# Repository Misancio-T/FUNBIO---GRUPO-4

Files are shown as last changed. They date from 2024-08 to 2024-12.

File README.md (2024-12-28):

<p align="center">
  <img src="[https://fundbio.github.io/images/pucp_upch.png]>
</p>

(https://postimg.cc/rDdD7Vwj)
---

<h1><p align="center"> Proyecto de FUNBIO - Equipo 4 ☕️ </p></h1>

¡Bienvenidos! Somos el Grupo 4 del Curso de Fundamentos de Biodiseño, Código: 1CAY41, dictado
en el semestre 2024-2 por la carrera de Ingeniería Biomédica PUCP - UPCH

## Temática de nuestro horario 📜

Lesiones Medulares

## Link de nuestro repositorio 🔗

 : github.com/Misancio-T/FUNBIO---GRUPO-4.git

## Link de nuestra página web 🌎

 : https://uyariy.tech

## Nos presentamos... 

<h3>ANGIE HUÁNUCO VÁSQUEZ (Coordinadora General)</h3>

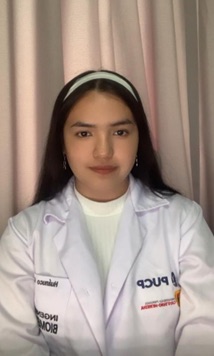
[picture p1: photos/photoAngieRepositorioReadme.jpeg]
fotoAngie
> 
> <h4> Me presento</h4>
>
> <p align="justify"> Soy estudiante de Ingeniería Biomédica con interés en el desarrollo y mejora de dispositivos médicos que permitan mejorar las condiciones de vida de las personas.  </p>
> <h4> Rol en el equipo</h4>
> <p align="justify"> Mi rol durante el curso es de Coordinadora General. Soy responsable de supervisar el avance del proyecto en su totalidad, asegurando que cada fase se ejecute según el plan establecido. Coordino las tareas entre los diferentes miembros del equipo, facilitando la comunicación y resolviendo cualquier problema que pueda surgir. Además, me encargo de la planificación de reuniones y la elaboración de los 'entregables' respecto al progreso del proyecto. </p>
> <h4> Rama de interés</h4>
> <p align="justify"> Procesamiento de señales e imágenes biomédicas. </p>

<h3>Misael Torres Bautista (Diseñador 3D)</h3>

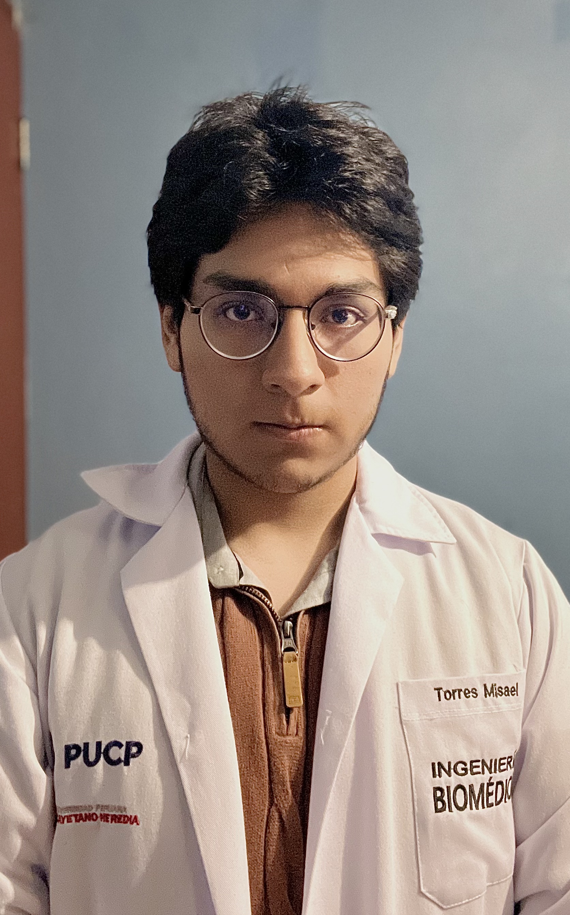
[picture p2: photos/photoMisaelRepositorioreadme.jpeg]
fotoMisael
> 
> <h4> Me presento</h4>
>
> <p align="justify"> Soy estudiante de Ingeniería Biomédica en la Pontificia Universidad Católica del Perú y la Universidad Peruana Cayetano Heredia. Busco desarrollar dispositivos médicos para mejorar la salud en el Perú. Mi objetivo es usar los conocimientos adquiridos a lo largo del curso para aplicar estas herramientas en un futuro.  </p>
> <h4> Rol en el equipo</h4>
> <p align="justify"> Mi rol en este proyecto es el de Diseñador 3D. Soy responsable de crear los modelos 3D basados en los bocetos y propuestas de solución desarrolladas por el equipo. Utilizo herramientas como INVENTOR, BLENDER, CINEMA 4D Y ULTIMAKER CURA para diseñar y preparar los modelos para su impresión. También me encargo de gestionar y actualizar el repositorio de GitHub del equipo.  </p>
> <h4> Rama de interés</h4>
> <p align="justify"> Ingeniería de tejidos y la biomecánica. </p>

<h3>Silvana Villegas Berrocal (Manufactura Digital)</h3>

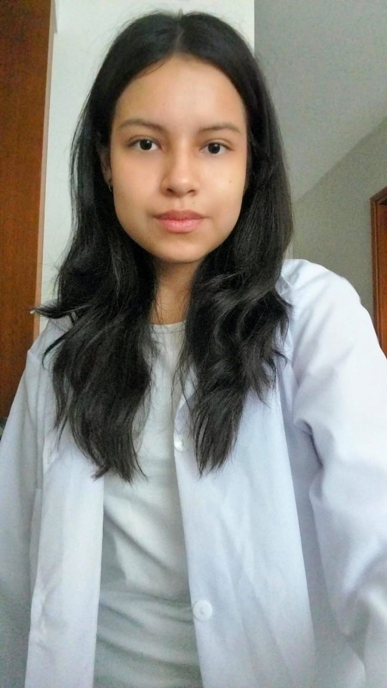
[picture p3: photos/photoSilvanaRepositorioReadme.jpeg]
fotoSilvana
> 
> <h4> Me presento</h4>
>
> <p align="justify"> Soy estudiante de Ingeniería Biomédica. Mi objetivo es la investigación de los cambios del cuerpo humano en diferentes ambientes para maximizar las capacidades físicas. </p>
><h4> Rol en el equipo</h4>
> <p align="justify"> Mi rol es diseñar y gestionar los procesos de manufactura digital, asegurando la calidad y precisión en la creación de prototipos. </p>
> <h4> Rama de interés</h4>
> <p align="justify"> Ingeniería molecular y celular así como sistemas biológicos. </p>

<h3>Sydnee Yampara Mamani (Prototipo Electrónico)</h3>

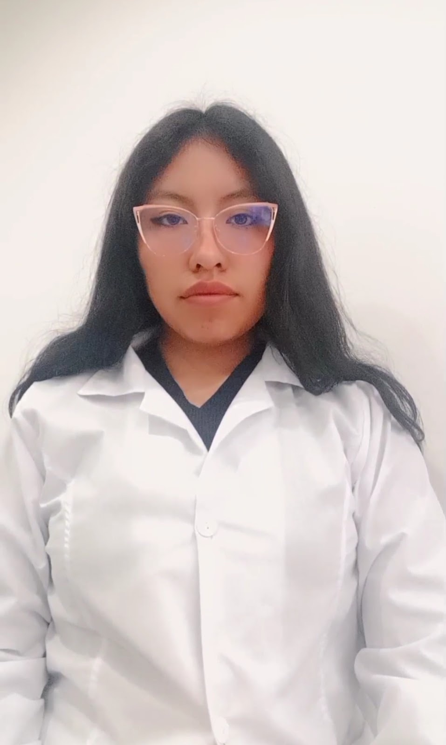
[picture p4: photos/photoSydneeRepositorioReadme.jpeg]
fotoSydnee
> 
> <h4> Me presento</h4>
> <p align="justify"> Soy estudiante de ing biomédica con objetivo de innovación e ideas de tecnología relacionada a la salud para la implementación descentralizada de equipos médicos y detección no invasiva de las distintas enfermedades. </p>
> <h4> Rol en el equipo</h4>
> <p align="justify"> Mi rol es diseñar y desarrollar prototipos electrónicos, incluyendo la selección de componentes y la integración de circuitos, para asegurar su funcionalidad y rendimiento. </p>
> <h4> Rama de interés</h4>
> <p align="justify"> Ingeniería clínica e ingeniería de tejidos. </p>

<h3>William Zamalloa Quispe (Diseño electrónico)</h3>

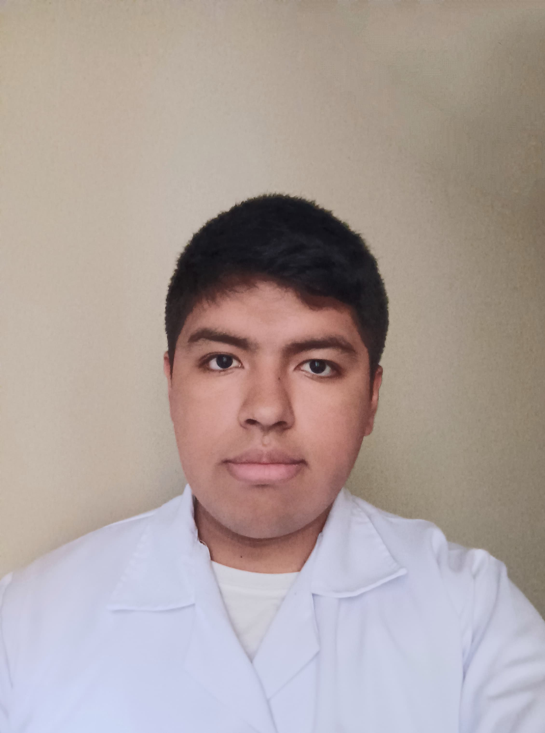
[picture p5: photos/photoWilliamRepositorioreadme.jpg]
fotoWilliam
> 
> <h4> Me presento</h4>
> <p align="justify"> Soy estudiante de ingeniería biomédica, poseo interés en la mejora y desarrollo de prótesis para el cuerpo humano, espero trabajar con prótesis sencillas y funcionales y con algunas más complejas y especializadas. </p>
> <h4> Rol en el equipo</h4>
> <p align="justify"> Mi rol es diseñar circuitos electrónicos utilizando software especializado, creando esquemas detallados y simulaciones para asegurar la eficiencia y funcionalidad de los prototipos. También administro y actualizo el repositorio de GitHub del equipo remotamente. </p>
> <h4> Rama de interés</h4>
> <p align="justify"> Biomecánica y desarrollo de prótesis avanzadas. </p>

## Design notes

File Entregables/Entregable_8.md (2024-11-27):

# Integración Hardware - Software - Manufactura Digital

## Introducción y Contextualización del Prototipo

### Descripción breve del Proyecto
El objetivo principal de este prototipo es desarrollar un sistema de retroalimentación sensorial artificial que mejore la propiocepción en personas con disminución de la percepción corporal,  se centra en proporcionar a estos pacientes un sistema que pueda suplir la retroalimentación sensorial pérdida y ayudarles a recuperar, en la medida de lo posible, la capacidad de moverse de forma segura y confiada.

Este sistema utiliza un dispositivo que mide la posición y el movimiento durante las fases de la marcha, ya sea al caminar o al estar de pie, y envía señales a unas bandas vibratorias que el usuario lleva puestas. Estas bandas vibran en tiempo real para proporcionar una retroalimentación táctil inmediata, alertando al usuario sobre su posición y movimiento.

### Problemática abordada

Este prototipo se centra en proporcionar a estos pacientes un sistema que pueda suplir la retroalimentación sensorial pérdida y ayudarles a recuperar, en la medida de lo posible, la capacidad de moverse de forma segura y confiada, todo esto a través de un sistema de feedback sensorial artificial que restaure la percepción corporal mediante retroalimentación táctil, promoviendo una rehabilitación más rápida y efectiva y aumentando la seguridad y el bienestar del paciente en su día a día.

La necesidad que motiva este proyecto es mejorar la calidad de vida de personas con lesiones medulares completas de tipo A que han perdido la capacidad de recibir retroalimentación sensorial y de controlar su motricidad mediante un dispositivo en forma de una cajita pequeña que va ajustada a una parte estratégica del pie. Esto nos ayudará a poder restaurar la pérdida de sensibilidad de nuestro paciente al momento de realizar bipedestación o marcha.  Esta pérdida de sensibilidad y control afecta significativamente su capacidad de moverse, caminar y mantenerse de pie de manera autónoma, lo que los hace depender de dispositivos de asistencia.

### Objetivos de la fase de integración

Lo que se espera al lograr integrar los componentes que forman parte de nuestra propuesta es asegurarnos de que los componentes del dispositivo (sensores, procesadores, baterías, etc) trabajen juntos de manera sincronizada para medir y registrar la proximidad del pie con el piso con precisión. A la vez, esperamos lograr que se logre comprobar los datos que los sensores envían para medir hacer las mediciones respecto a las pisadas del paciente para poder corregir errores de lectura. Finalmente, deseamos evaluar que el dispositivo sea compatible con las condiciones reales de uso, comprobando que la integración de sus componentes le permita operar correctamente en entornos de prueba similares a su aplicación final.

## Componentes del Prototipo

### Lista de componentes principales

**Componentes en la parte del pie**

- **Batería 3.7V, 720 mAh Li-Po:** Actúa como la fuente de energía para esta sección del prototipo, suministrando alimentación al Atom Matrix.
- **LiPo Rider Plus:** Este módulo sirve como intermediario entre la batería y el Atom Matrix, facilitando la carga de la batería a través de un puerto USB tipo C.
- **Atom Matrix:** Es el "cerebro" del prototipo. Integra un acelerómetro MPU-6886 que captura datos en los ejes X, Y y Z en tiempo real, así como un ESP32 PICO, un microcontrolador compacto utilizado para enviar los datos por medio de Bluetooth. Además, cuenta con una pantalla de luces LED que puede utilizarse de distintas maneras, como un indicador visual adicional, proporcionando así feedback tanto para el paciente como para el terapeuta.

**Componentes en la parte del brazo**

- **Motores Vibradores Tipo Moneda:** Similar a los que se usan en teléfonos móviles, estos motores se emplea para proporcionar retroalimentación sensorial en el brazo del usuario.
- **Batería 3.7V, 720 mAh Li-Po:** Actúa como la fuente de energía en esta sección del prototipo, suministrando alimentación al ESP32 Super Mini.
- **Módulo TP4056:** Es una versión más sencilla que el LiPo Rider Plus y permite cargar la batería Li-Po y alimentar el ESP32 Super Mini.

### Interacción entre componentes

Los componentes principales que interactúan en este prototipo son el Atom Matrix, que incluye un ESP32 PICO, y el ESP32 Super Mini ubicado en el brazo. La comunicación entre ambos se realiza mediante programación Bluetooth, estableciendo un sistema maestro-esclavo para la transmisión y recepción de datos entre los dispositivos.

### Diagrama de integración

<p align="center">
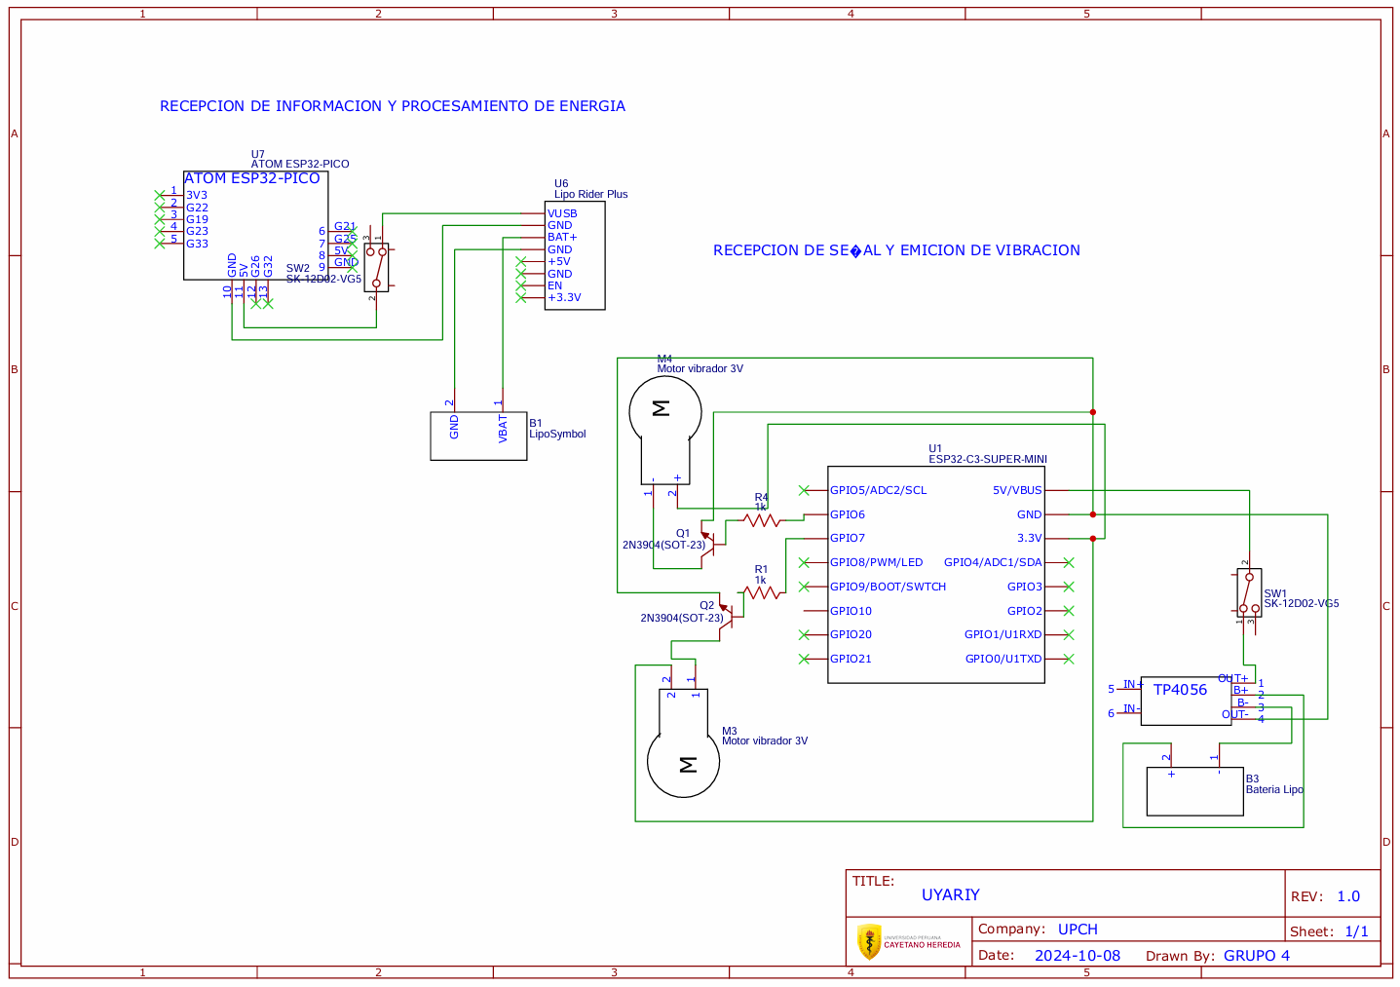
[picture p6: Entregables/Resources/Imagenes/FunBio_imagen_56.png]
Esquema Electrónico

</p>

## Proceso de Integración

### Plan Inicial de Integración

**- Paso 1:** Desarrollo del Sistema en el Pie

Configuración del ATOM PICO ESP32 para medir ángulos y convertirlos en grados de inclinación que al tener incluído el microcontrolador podemos visualizar los datos en tiempo real mediante un monitor serie con el objetivo de tener mediciones precisas y consistentes.

Para la programación del microcontrolador (pie) creamos un programa para leer datos del sensor y transmitirlos por Bluetooth al dispositivo esclavo.

Se prueban datos simulados desde el sensor a una laptop.

**- Paso 2: Desarrollo del Sistema en el Brazo (dispositivo esclavo)**

Programar el receptor Bluetooth para recibir datos enviados por el módulo del pie.  Posteriormente integrar y probar el motor de vibración para generar pulsos en función de los datos.  

Se probó simulando la recepción de ángulos y activar las luces led, momentáneas, correctamente.

**- Paso 3: Comunicación Bluetooth**

Configurar el emparejamiento del módulo transmisor del pie con el receptor del brazo para verificar la estabilidad y velocidad de la conexión Bluetooth

### Pruebas Intermedias

**1. Prueba unitaria del sensor:**

   Confirmar que el sensor mide correctamente los ángulos de inclinación.  

**2. Prueba de transmisión Bluetooth:**  
   
   Evaluar la precisión y latencia de los datos enviados desde el pie al brazo.  

**3. Prueba del motor de vibración:**  
   
   Ajustar la intensidad y duración de las vibraciones para que sean perceptibles sin ser incómodas.  

### Objetivos

1. Obtener mediciones angulares precisas del pie durante diferentes pisadas.

2. Lograr una transmisión de datos Bluetooth con baja latencia y sin interrupciones.

3. Generar una retroalimentación háptica en el brazo que sea intuitiva y fácil de interpretar.

4. Implementar un diseño ergonómico y funcional para ambos módulos.

### Desafíos y ajustes realizados

**1. Calibración del Sensor de Ángulo**

- Desafio

La lectura del sensor era inconsistente debido a interferencias de movimiento no deseado y ruido en los datos, también el cuestionamiento de medida entre el ángulo o la altura.

- Ajuste Realizado

Ajuste de los valores iniciales mediante un proceso de calibración manual para establecer un punto de referencia (offset) y decisión de medida a angulo de giro..

### Revisión de compatibilidad y sincronización

<p align="center">
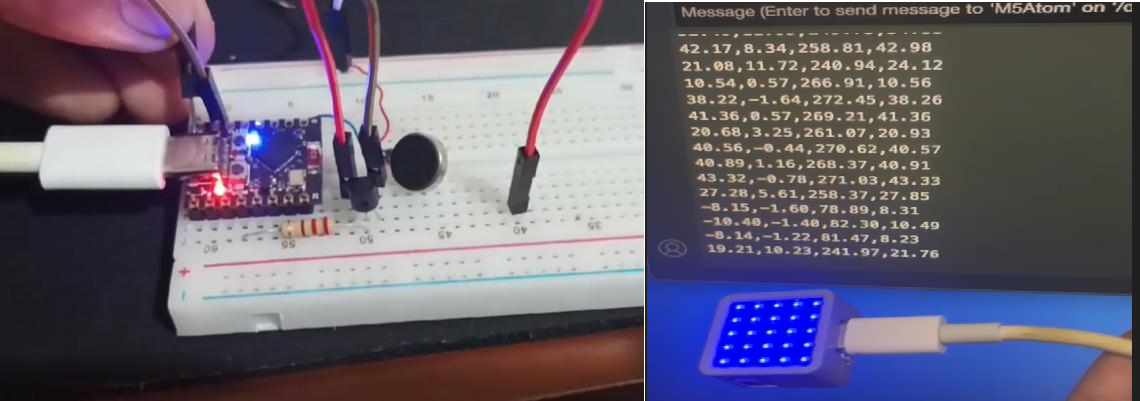
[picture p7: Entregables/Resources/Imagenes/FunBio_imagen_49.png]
Revision de componentes

</p>

## Pruebas y Verificación

### Descripción de pruebas funcionales

Los microcontroladores usados requieren más programación, para ello se usaron ejemplos presentes en Arduino y luego de comprobar su funcionamiento se procedió a probar el de componentes, en el caso de los motores vibradores para comprobar su funcionamiento se conecto el cable positivo al terminal de 3.3v de uno de los microcontroladores y el cable negativo a GND, con ello probamos que todos los componentes son funcionales y están listos para el ensamblaje en conjunto.

### Resultados de pruebas

Las primeras pruebas se esperaba lograr la activación del motor con un pin del microcontrolador pero estas pruebas resultaron fallidas debido a que se intentó usar un protoboard para realizar las conexiones del esp32 C3 con el motor vibrador y no se podía porque el esp32 no se podía conectar bien al protoboard, para ello fue necesario soldar los componentes al esp32 para comprobar su funcionamiento, otro contratiempo fue que los motores vibradores tienen un cable muy delgado que complica las conexiones además de el soldar el motor al resto de componentes, para ello fue necesario realizar un intercambio de cables en el motor por uno más gruesos para así trabajar de una mejor manera.

### Evaluación de desempeño

Nuestro prototipo consta de 2 partes, un dispositivo que irá instalado en el pie y otro que irá instalado en el brazo, debido a que usamos un atom matrix en el dispositivo del pie, ese prototipo cumple con el objetivo inicial debido a que ya detecta el movimiento y cumple su parte en la medición, el dispositivo en el brazo es más complejo por la conexión de distintos componentes, pero ya esta en la ultima fase, y teoricamente tambien cumplira los objetivos planteados.

## Conclusiones y Próximos Pasos

### Resumen de logros

**Desarrollo del sistema en el pie:**

- Configuración exitosa del ATOM ESP32 para medir y transmitir los datos angulares en tiempo real mediante Bluetooth permitiendo la presión y latencia de los datos enviados, esto se logró por el proceso de calibración manual para establecer un punto de referencia
- Integración y prueba, logrando mediciones concretas de inclinación en los ejes 
- Diseño funcional que incluye la pantalla LED del ATOM para retroalimentación visual al paciente y terapeuta
- Cumplimiento del objetivo inicial, mide el movimiento
- Prueba de la recepción de ángulos y activar las luces led momentáneamente exitosa

**Desarrollo del sistema del brazo:**

- Programación del receptor Bluetooth para recibir datos enviados desdes el dispositivo del pie 
- Integración del motor vibrador exitosamente, sirviendo como mecanismo de retroalimentación háptica, genera los pulso en función de los datos enviados, se encuentra en la última fase y se espera que cumpla los objetivos 
- Ajustes en la intensidad y duración de las vibraciones para asegurar una experiencia cómoda y efectiva para el paciente. 

**Integración de comunicación Bluetooth:**

- Establecimiento exitoso de un sistema maestro-esclavo entre los módulos del pie y del brazo, con transmisión de datos luida y de baja latencia.

**Prueba de componentes:**

- Verificación de las baterías, sensores, motores vibradores y módulos de Bluetooth
- Se logró solucionar los problemas de conexión mediante la soldadura de los componentes y sustitución de cables para mejorar la estabilidad. 

### Aspectos por mejorar: Discutir qué problemas aún existen o qué componentes requieren ajuste adicional

1. Calibración y estabilidad del sensor de ángulos

Aunque el sensor ya puede medir ángulos, para obtener mejor precisión de los datos es necesario optimizar su calibración para garantizar lecturas más precisas, sobre todo que responda a las condiciones dinámicas del movimiento del paciente. 

2. Sincronización entre los componentes

Aunque el sistema maestro-esclavo entre ambos componentes es exitoso, se podrían detectar ligeros retrasos en la transmisión de los datos.

3. Duración de la batería:

La autonomía actual de la baterías puede ser insuficiente para que se prolongue por toda las sesiones de rehabilitación

4. Pruebas en condiciones reales

Hasta la fecha no hemos podido probar nuestro componentes en situaciones reales para los casos de pacientes en los que nos enfocamos, por ahora solo se está haciendo simulaciones, esperamos realizar pruebas en condiciones más cercanas a nuestros pacientes para identificar problemas y posibles limitaciones con el objetivo de la mejora y avance de nuestro proyecto. 

Aunque nuestro prototipo ha alcanzado un nivel satisfactorio a nuestras posibilidades, estos aspectos se pueden mejorar. Se espera que con las mejoras más adelante se puedan realizar las mejoras necesarias para la calibración, precisión, y duración de la batería. Si se logra solucionar este dispositivo será más preciso y confiable, garantizando así el objetivo y funcionamiento de Uyarai 

### Siguientes fases del desarrollo: Describir los pasos próximos y cómo se enfocarán en mejoras o implementaciones futuras

Las siguientes fases del desarrollo de nuestro prototipo se enfocarán en resolver los problemas técnicos de los componentes, se espera optimizar el diseño para que sea más accesible a todos los pacientes. Se espera además extender la funcionalidades del dispositivo para mejorar la experiencia entre el paciente y terapeuta Además se espera avanzar a la etapa de aprobación y pruebas clínicas. Esto permitirá que el prototipo evolucione hacia una solución más confiable para mejorar de esta forma la calidad de la vida de las personas con lesiones medulares.

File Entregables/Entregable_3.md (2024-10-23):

# Coherencia problemática- Propuesta solución

## Problemática

### Contexto

En entorno de nuestra problemática se basa en las lesiones medulares, estas son altamente frecuentes en situaciones de alto riesgo, como accidentes de tráfico, caídas desde alturas, accidentes deportivos y también pueden ocurrir por causas internas como enfermedades o infecciones. Estas lesiones afectan a gran cantidad personas a nivel mundial cada año, provocando discapacidades severas que afectan tanto la movilidad física como la calidad de vida en general. Este tipo de trauma es uno de los más devastadores en cuanto a su impacto en la autonomía y bienestar del paciente, ya que compromete funciones vitales como el control del movimiento voluntario, la sensibilidad, la respiración, la función vesical e intestinal, etc.

Las lesiones medulares representan una amplia relevancia en el campo de la ingeniería biomédica debido a su impacto en la directo en la vida de los pacientes dentro y fuera de centros de la salud, además, el desarrollo de nuevas soluciones son necesarias para ayudar a reparar las deficiencias médicas a través de tecnologías que ayudan a acelerar los tratamientos y optimizan los resultados a largo plazo de los pacientes, tales como  facilitar su rehabilitación y  ayudarles a recuperar el mayor grado de funcionalidad corporal, tanto física como  biológicamente.

### Definición del Problema

Pérdida de retroalimentación sensorial y control motor en personas con una lesión medular tipo A (lesión completa) en la parte inferior del cuerpo, particularmente durante la bipedestación y la marcha.

### Impacto

**Impacto en los usuarios**

El problema de la pérdida de retroalimentación sensorial y control motor en personas con una lesión medular completa de tipo A tiene un impacto significativo tanto en la vida de los pacientes como en los sistemas de salud. Uno de los efectos principales es la pérdida de movilidad ya que la persona pierde la capacidad de controlar los músculos en las piernas, lo que significa que no puede caminar ni mantenerse de pie sin asistencia, generando de esta forma una escasa independencia de la persona.

Por otro lado, los pacientes en etapa de tratamiento realizan la bipedestación  y la marcha como ejercicios clave en su recuperación, estas actividades son esenciales pero complicadas de realizar ya que dependen de la retroalimentación sensorial (información que el cerebro recibe del cuerpo sobre la posición de las extremidades) y del control motor, la pérdida de estas funciones implica que la persona no pueda percibir la posición de sus piernas, no puede hacer ajustes automáticos al equilibrio, ni realizar movimientos coordinados para caminar.

La pérdida de la movilidad está asociada con ansiedad, depresión y una disminución de la calidad de vida. La adaptación a una nueva realidad sin la capacidad de caminar o moverse de forma independiente puede ser devastadora, los estudios muestran que entre el 20% y el 40% de las personas con una lesión medular experimentan algún grado de depresión clínica debido a estos cambios drásticos en su vida. [[1]](https://github.com/Misancio-T/FUNBIO---GRUPO-4/blob/main/Entregables/Entregable_3.md#bibliograf%C3%ADa)

**Impacto en el sistema de salud**

El sistema de salud tiene una gran responsabilidad y carga al tratar a personas con este tipo de lesiones, sobre todo en nuestro país, donde la implementación de nuevas tecnologías es escasa y se suelen realizar los tratamientos convencionales que tiene como resultado una evolución lenta en la mejora de los pacientes.

Los pacientes con lesiones medulares requieren terapia física y ocupacional extensiva para maximizar su independencia, según el NSCISC,aproximadamente el 80% de los pacientes con lesiones medulares requieren asistencia para actividades de la vida diaria, ya sea con sillas de ruedas o dispositivos de asistencia como exoesqueletos robóticos y la ayuda de cuidadores o fisioterapeutas para tareas diarias. Sin Embargo, en Perú existe un notable déficit de profesionales frente a la creciente necesidad de rehabilitación, especialmente en zonas rurales y alejadas. [[2]](https://github.com/Misancio-T/FUNBIO---GRUPO-4/blob/main/Entregables/Entregable_3.md#bibliograf%C3%ADa)

## Propuesta de solución

### Descripción de la Solución

**Nuestra propuesta de solución es un Dispositivo de Alerta de Pasos en base a una retroalimentación sensorial.** Este estaría compuesto por cuatro partes: dos en los pies (dispositivos de deteccion de movimiento con sensores) y dos en los brazos (Receptores vibradores). Los sensores detectan cuándo el pie se inclina al realizar una fase de la marcha y lanza una señal hacia el dispositivo en los brazos. El dispositivo en los brazos recibe la señal, lo cual ocacionara que vibre para alertar al usuario que efectivamente ha completado una fase de la marcha, proporcionando una retroalimentación sensorial al usuario, el cual no llega a tener sensación física en sus pies debido a una lesión medular o uso de prótesis.

### Características del Prototipo
**Emplea:** Dos acelerómetros MPU6886, estos se encontrarán sujetos a la parte superior del empeine del pie, y se encargará de detectar mediante giroscopio el angulo de inclinacion del pie.

**Transmisión inalámbrica con ESP32:** La señal recibida por los sensores en los pies se enviarán de forma inalámbrica desde los sensores al receptor en los brazos usando la conectividad Wi-fi/Bluetooth de este chip.

**Receptor vibratorio en el brazo:** Dos dispositivos vibratorios compactos, que pueden llevarse como bandas, emitirán una vibración en cada brazo cuando se reciba la señal del sensor del pie, alertando al usuario de que ha dado completado una fase de la marcha.

**Fuente de energía:** Baterías de Litio, son pequeñas y más sencillas de implementar en nuestro dispositivo que busca la simplicidad.

### Beneficios

**Mejorar la percepción del movimiento:** El usuario aumentaría su conciencia sobre la posición de sus pies durante la marcha, lo cual es bastante necesario para una persona con lesión medular o amputaciones las cuales no pueden llegar a sentir sus pies.

**Facilidad de rehabilitación:** Ayudaría al usuario a desarrollar y ajustar su marcha durante la rehabilitación, al recibir esta retroalimentación sensorial en tiempo real cuando sus pies están realizando la marcha. Hay dispositivos que brindan esta retroalimentación sensorial, sin embargo la señal se suele envíar a lugares muy cercanos y no incluyen a usuarios que pueden tener mayor sensibilidad en una zona alejada a la planta de los pies.

**Diseño no invasivo y discreto:** A comparación de otros exoesqueletos grandes, o que requieren gran cantidad de componentes y cables, este sería ligero, fácil de usar y no requeriría cables, todo ello facilitando su integración en el día a día del paciente.

**Asequibilidad:** Comparando con otros dispositivos más complejos de rehabilitación, nuestra propuesta es más económica y de fácil implementación, al usar componentes de fácil acceso en el mercado y que son viables técnicamente.

### Viabilidad Técnica

Hemos evaluado el desarrollo del prototipo y este es técnicamente viable utilizando componentes disponibles en el mercado, como:

- ESP32 para la conectividad inalámbrica y procesamiento de señales.
- Acelerómetros ya ampliamente utilizados en diversos dispositivos para las detecciones de ángulos y posición
- Baterías pequeñas como las baterías de litio, pueden proporcionar la energía necesaria para el funcionamiento continuo del dispositivo.
- Conocimientos básicos de electrónica y programación para integrar los sensores con el ESP32, configurar el sistema de transmisión y programar el mecanismo de vibración en el receptor de los brazos.
- Impresión 3D o adaptación de materiales para crear las carcasas de los componentes, como las plantillas que se colocarán en los pies y el dispositivo vibratorio en los brazos.

## Coherencia

### Contexto del Proyecto

La propuesta de solución va directamente relacionada con la temática de lesiones medulares, específicamente con pacientes que sufrieron la pérdida de sensibilidad y movilidad en las extremidades inferiores. Según el caso analizado, el paciente presenta una lesión medular entre D11 y D12 que afecta su capacidad de sentir sus piernas y caminar, lo que limita su independencia y avance de tratamiento.

La propuesta de solución es necesaria porque después de una lesión medular , los pacientes tienden a perder la capacidad sensorial que afecta su equilibrio, postura y capacidad de caminar. La implementación de un sistema feedback sensorial artificial puede ayudar en gran medida a cubrir la falta de señales sensoriales y mejorar la calidad de vida y tratamiento del paciente.

Estudios han demostrado que el feedback sensorial en rehabilitación neurológica es una manera eficaz de mejorar la percepción corporal y reducir la dependencia visual en pacientes con lesiones medulares. Este tipo de tecnología integra la ingeniería biomédica al utilizar dispositivos portátiles y tecnología de comunicación inalámbrica para proporcionar una retroalimentación sensitiva en tiempo real. [[3]](https://github.com/Misancio-T/FUNBIO---GRUPO-4/blob/main/Entregables/Entregable_3.md#bibliograf%C3%ADa)

### Objetivos del Proyecto

El objetivo general del proyecto es desarrollar un sistema de feedback sensorial artificial que mejore la propiocepción y la capacidad de movilidad de paciente con lesiones medulares. Esto se logrará mediante la implementación de un dispositivo que ayuda al paciente a complementar la percepción sensorial, contribuyendo así al avance del tratamiento, la rehabilitación y la calidad de vida de los pacientes. Se busca que los pacientes puedan recuperar parte de su independencia funcional en sus extremidades inferiores, mejorando su equilibrio y estabilidad además de tener un impacto positivo en su salud mental del paciente que puede verse deteriorada por las razones ya mencionadas.

**Objetivos específicos**

- Diseño de dispositivos de deteccion con acelerómetros, los sensores del tipo acelerómetro son eficaces para detectar ángulos y movimiento en dispositivos portátiles, este brinda información crítica sobre las fases de la marcha del paciente.
- Desarrollar el diseño de bandas vibratorias para el feedback sensorial que proporciona estímulos vibratorios específicos en respuesta a las señales captadas por los sensores, simulando la retroalimentación sensorial que falta debido a la lesión medular.
- La comunicación inalámbrica entre los dispositivos, se refiere a implementar un sistema de comunicación eficiente y sin cables que permite una rapidez en la interacción de los diferentes componentes del dispositivo.
- Optimizar materiales para entornos de bajos recursos, el diseño de soluciones asequibles y portátiles es crucial para provincia y áreas rurales donde el acceso a tecnologías avanzadas es limitado.
- Aprobar la eficacia en pruebas clínicas necesarias asegurando de esta forma que el sistema sea seguro y efectivo, cumpliendo los requisitos médicos obligatorios y regulatorios para el uso de paciente con lesiones medulares en orden de ayudar a la medicina a través de la ingeniería biomédica.

### Justificación del Prototipo

La propuesta de solución destaca frente a otras opciones debido a su capacidad de proporcionar retroalimentación sensorial en tiempo real. En comparación con la estimulación eléctrica funcional (FES) que utiliza impulsos eléctricos para activar nervios periféricos que controlan los músculos, enfocándose en la activación muscular, el feedback sensorial propuesto se centra en simular la sensación perdida, brindando una percepción sensorial en tiempo real que ayuda a reconectar con su cuerpo. Este producto no solo mejora la movilidad, sino que también reduce el riesgo de caídas y genera una mayor autonomía.

Además, resulta tener efectos más prometedores, con sensores del tipo acelerómetro que se enfocan en restaurar la retroalimentación sensorial, el uso de estos dispositivos no es  invasivo, ya que simplemente se colocan en el calzado y la banda vibratoria en las extremidades superiores . Por esta razón, fortalece la conexión cerebral-sensorial, facilitando una mejor integración de la percepción corporal y permitiendo al paciente compensar la pérdida de movilidad con mayor consciencia de su cuerpo en el espacio. El uso de feedback sensorial mediante vibraciones tiene un riesgo mucho menor de fatiga muscular ya que no implica contracción muscular directa, esto permite que el sistema pueda utilizarse durante periodos más largos sin causar agotamiento. [[4]](https://github.com/Misancio-T/FUNBIO---GRUPO-4/blob/main/Entregables/Entregable_3.md#bibliograf%C3%ADa)

A diferencia de otros dispositivos médicos más complejos, como los que utilizan estimulación eléctrica o prótesis sofisticadas, los componentes de nuestra propuesta son más económicos, convirtiéndose en una propuesta accesible para diferentes contextos socioeconómicos. Los acelerómetros y las bandas vibratorias son tecnologías accesibles que pueden ser fabricadas con materiales de bajo costo, sin perder la eficiencia de su propósito.El mantenimiento y operación sencilla de los dispositivos, al no depender de estimulación eléctrica invasiva o complejos mecanismo de control reduce los costos de mantemiento.

La simulación de sensaciones perdidas en los pacientes permite captar la posición y los movimientos del pies, mientras que las bandas vibratorias pueden proporcionar retroalimentación táctil en tiempo real, simulando la sensación de contacto con el suelo y la respuesta sensorial pérdida.

Al mejorar la capacidad sensorial y propioceptiva de los pacientes, se les brinda una mayor autonomía en sus actividades diarias. Al sentirse más seguros al caminar y moverse, pueden desarrollar una mayor independencia, lo que impacta directamente en su calidad de vida. La simplicidad y accesibilidad del dispositivo lo hace aceptable para uso cotidiano, permitiendo que los pacientes lo utilicen en múltiples escenarios sin la necesidad de equipos especializados o supervisión médica constante.

Los estudios han demostrado que el feedback sensorial mejora la plasticidad neuronal, lo que ayuda a que el cerebro se readapte y fortalezca las conexiones neurales pérdidas, esto contribuye a una rehabilitación más efectiva. Con nuestro dispositivo el cuerpo podrá percibir su posición y movimiento en el espacio, el cerebro recibe información aparecida sobre la posición de las piernas a través de la retroalimentación vibratorias proporcionada por las bandas, mejorando directamente el equilibrio del paciente, reduciendo el riesgo de caídas en la rehabilitación y mejorando la capacidad de caminar independientemente.

Nuestra propuesta no está limitada a pacientes con las extremidades presentes, sino también en el caso de pacientes con amputaciones o trastornos congénitos, este tipo de feedback sensorial artificial puede ser integrado en procesos para proporcionar sensaciones táctiles en puntos clave de contacto. Los sensores pueden ser colocados en las superficies del calzado de las prótesis, mientras que las bandas pueden ser colocadas en  partes estratégicas del cuerpo para devolver la sensación de presión al paciente. Esta simulación de la sensación de la extremidad perdida es crucial para mejorar la integración de la prótesis ayudando a los  pacientes a tener control de sus movimientos y a sentirse más conectados con la prótesis.

### Alineación con el Problema

Nuestro prototipo aborda la pérdida de retroalimentación sensorial y control motor en personas con lesiones medulares, especialmente durante la bipedestación y la marcha. Al utilizar dispositivos de deteccion con acelerómetros, se capta la inclinacion y el movimientos de los pies cuando entran en contacto con la superficie, información crítica que los pacientes no pueden percibir naturalmente. Estos sensores recopilan datos sobre la posición y los ángulos, aunque los pacientes no pueden sentir directamente esta información los datos son enviados a través de bandas vibratorias, estas vibraciones actúan como una forma de sensor artificial, proporcionando al cerebro información sobre la posición y postura, ayudando al equilibrio del paciente.

## Resumen

### Problema y propuesta de solución
El problema aborda la **pérdida de retroalimentación sensorial y control motor** de personas con **lesiones medulares completas de tipo A**, lo que afecta la capacidad de caminar y mantenerse de pie. Esta falta de sensibilidad genera una dependencia de dispositivos de asistencia que afecta negativamente la calidad de vida y de tratamiento del paciente que retrasa su rehabilitación.

La propuesta de solución es un **sistema feedback sensorial artificial** que utiliza **un dispositivo de medida de posicion y bandas vibratorias.** El dispositivo capta las fases de la marcha al caminar o estar de pie, que envían señales a las bandas vibratorias proporcionando retroalimentación táctil en tiempo real, ayudando a restaurar la percepción corporal perdida. Este dispositivo **mejora la propiocepción reduciendo el riesgo de caídas,** y **permite al paciente recuperar su autonomía** mejorando su equilibrio y estabilidad.

### Resultados esperados

El desarrollo del dispositivo feedback sensorial busca mejorar la **propiocepción y movilidad** de los pacientes con lesiones medulares, permitiendo que recuperen parte de su independencia. Se espera que los pacientes puedan caminar con más confianza y estabilidad, al mismo tiempo que puedan mejorar su estabilidad mental y calidad de vida.

Para testear el prototipo, se podría realizar **pruebas clínicas** con pacientes en etapas de rehabilitación. Se mediría la mejora de **equilibrio, capacidad de marcha,** y la **reducción de la dependencia visual.** El testeo incluiría la comparación del rendimiento del paciente con y sin el dispositivo, midiendo la precisión de la retroalimentación sensorial y su impacto en la **reducción de caídas.**

### Proximos Pasos

- Desarrollo y construcción de prototipo: diseñar y ensamblar las plantillas con sensores y las bandas vibratorias.
- **Validación técnica:** realizar pruebas preliminares para asegurar la funcionalidad y comunicación inalámbrica.
- **Pruebas clínicas:** evaluar el prototipo en el paciente, midiendo la efectividad del equilibrio y movilidad.
- **Optimización:** Utilizar componentes de fácil adquisición para hacerlo más accesible y adaptable a distintos usuarios.

## Bibliografía

- [1] Katlin R. Schultz, Linda R. Mona, Rebecca P. Cameron. Mental Health and Spinal Cord Injury: Clinical Considerations for Rehabilitation Providers. 2022. https://www.ncbi.nlm.nih.gov/pmc/articles/PMC9046713/
- [2] World Health Organization: WHO. (2024b, abril 16). Spinal cord injury. https://www.who.int/news-room/fact-sheets/detail/spinal-cord-injury
- [3] Volker Dietz, Karim Fouad, Restoration of sensorimotor functions after spinal cord injury, Brain, Volume 137, Issue 3, March 2014. https://academic.oup.com/brain/article/137/3/654/389117
- [4] La estimulación eléctrica funcional (FES) para las lesiones de la médula espinal. MSKTC. (s. f.). https://msktc.org/sci/factsheets/la-estimulacion-electrica-funcional-fes-para-las-lesiones-de-la-medula-espinal

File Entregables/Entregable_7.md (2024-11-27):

# Iteración y Reporte de Pruebas

## Iteración

### Hardware Electronico

#### Diseño esquemático del circuito (corregido)

<p align="center">
Esquema Electrónico (corregido)
</p>

#### Ejecucion del codigo arduino

**Codigo en Arduino para probar los componentes**

<p align="center">
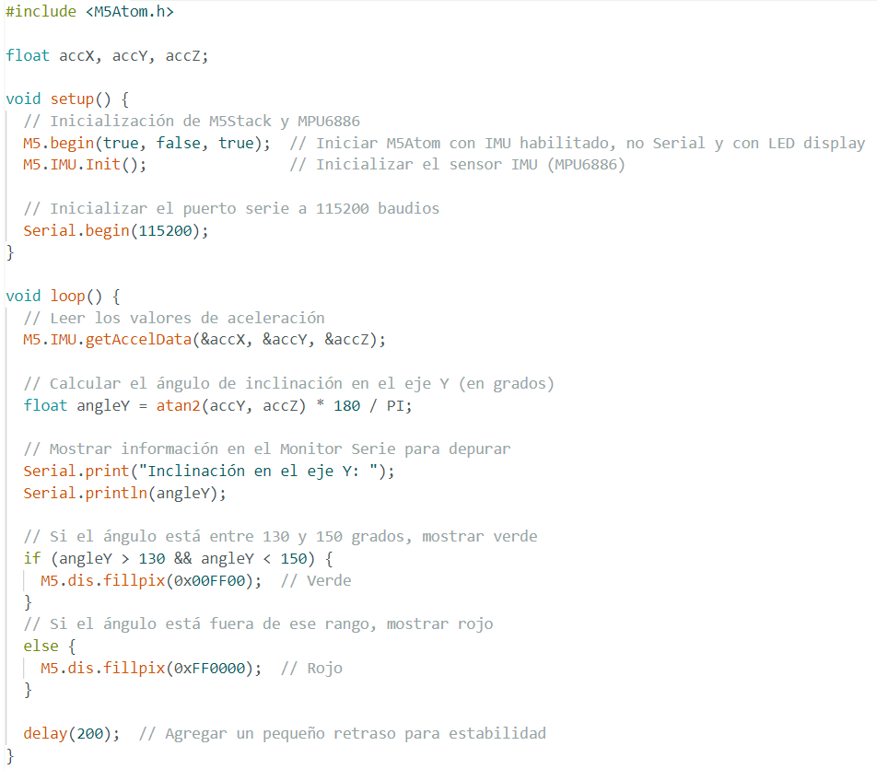
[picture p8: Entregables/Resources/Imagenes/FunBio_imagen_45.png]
Codigo de Programacion

</p>

#### Prototipado electrónico

<p align="center">
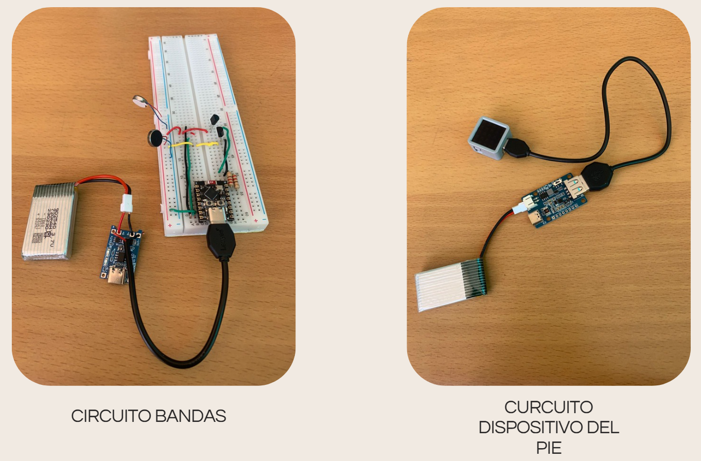
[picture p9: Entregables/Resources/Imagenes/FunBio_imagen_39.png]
Esquema Electrónico

</p>

### Diagrama de flujo del codigo final

Para hacer una introduccion al sofware vamos a presentar nuestro **Diagrama de Flujo de Datos** de nuestro codigo

Dispositivo de Medicion

<p align="center">
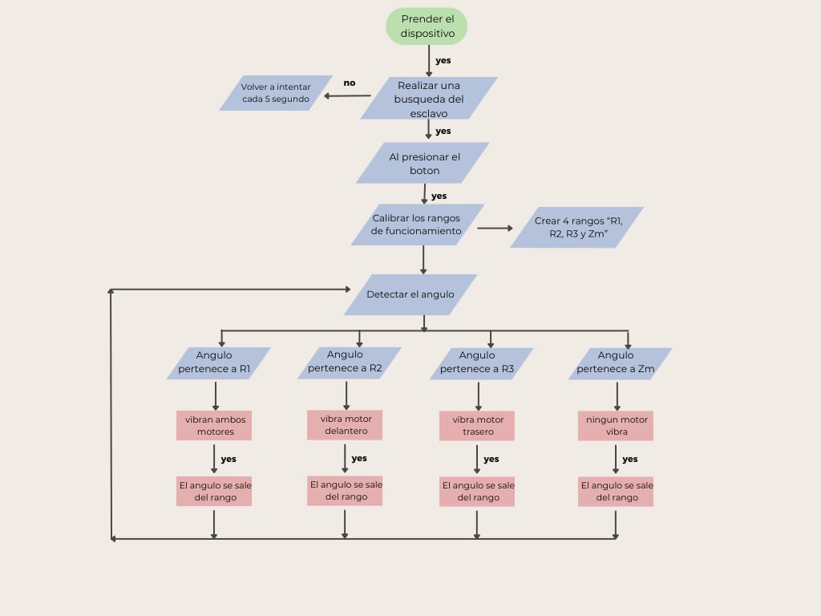
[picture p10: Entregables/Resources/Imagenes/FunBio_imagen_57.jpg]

</p>

Dispositivo sensorial

<p align="center">
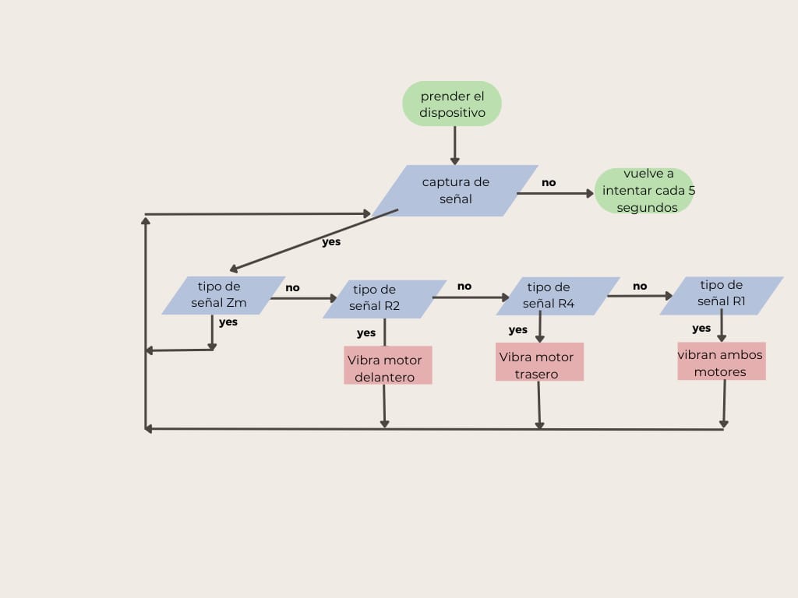
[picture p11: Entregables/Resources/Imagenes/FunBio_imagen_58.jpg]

</p>

### Impresión 3D

#### Modelos 3d Aprobados

- Dispositivo del Pie

<p align="center">
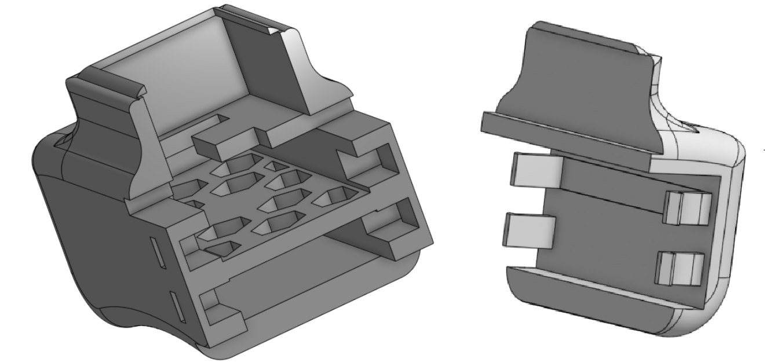
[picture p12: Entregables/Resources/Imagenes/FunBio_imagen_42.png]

</p>

- Dispositivo del Brazo

<p align="center">
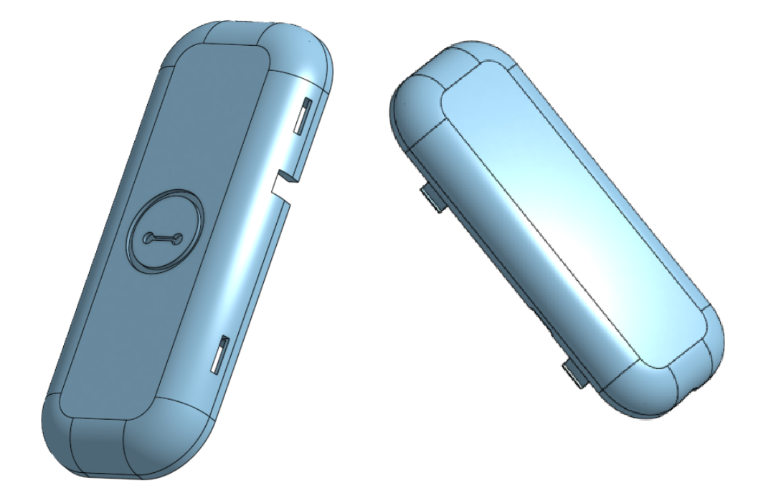
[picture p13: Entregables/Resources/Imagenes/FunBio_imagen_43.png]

</p>

#### Modelado digital del prototipo

- Dispositivo del Pie

<p align="center">
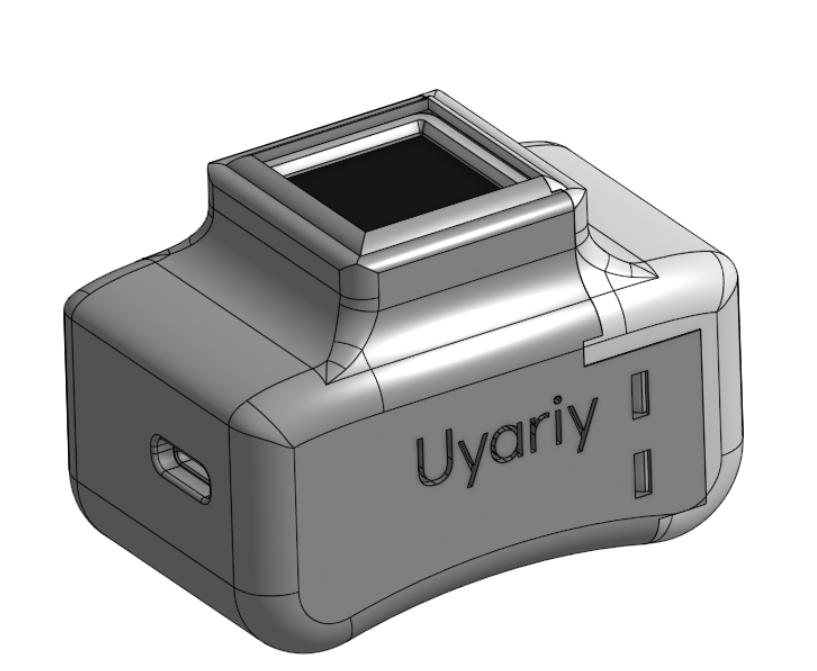
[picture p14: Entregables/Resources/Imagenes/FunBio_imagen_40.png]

</p>

- Dispositivo del Brazo

<p align="center">
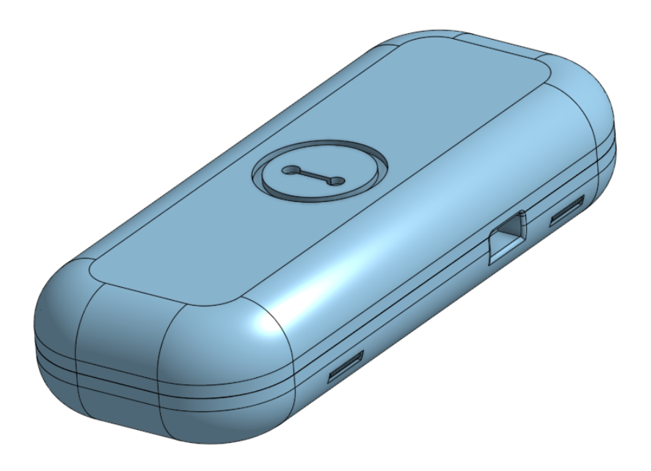
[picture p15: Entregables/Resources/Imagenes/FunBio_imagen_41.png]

</p>

## Reporte de pruebas, retos y limitación de los componentes

### Evaluar funcionalidad y usabilidad por componente

#### Para los componentes que se utilizaran para las bandas en los brazos:

- **Batería de litio:** la batería de litio proporciona la energía necesaria para el sistema, asegurando que la retroalimentación sensorial esté disponible de manera constante. La capacidad debería ser suficiente para mantener el sistema activo durante el tiempo necesario para sesión de rehabilitación sin interrupciones.
- **Lipo Rider Plus:** Este modulo de carga es ideal para facilitar la conexión entre la batería y el sistema EPS 32. Ofrece una interfaz a carga de un puerto USB, asegura una administración de energía eficiente y protege el sistema contra picos de voltaje. Su tamaño es compacto y su diseño modular aumentan la usabilidad, ya que permite que el dispositivo sea recargado fácilmente.
- **Motores vibradores:** Los motores son fundamentales para proporcionar la retroalimentación háptica que el usuario necesita para sentir las pisadas. Colocados estratégicamente en puntos claves de las bandas, pueden dar señales sensoriales claras en función de la presión detectada en los pies. Su respuesta rápida a través de bluetooth al sentir las pisadas además de su bajo consumo de energía los hacen adecuados para este tipo de retroalimentación.
- **ESP32:** este microcontrolador es esencial para procesar los datos del sistema y controlar de manera eficiente el momento de los motores vibradores en tiempo real. Su conectividad WIFI y Bluetooth permite que la comunicación inalámbrica entre nuestro dispositivo y las bandas en los brazos sean efectivas. La flexibilidad y el bajo consumo del ESP32 son ventajas claves, soportan la batería y facilitan el envío y recepción de señales de manera eficiente.

#### Para el dispositivo situado en el pie

- **Atom MPU 6886 ESP32:** Este microcontrolador integrado con un sensor de movimiento (MPU 6886) es fundamental para medir la orientación, aceleración y posibles cambios de posición del pie. Su capacidad para procesar los datos permite una rápida interpretación de los estos para que el sistema proporcione retroalimentación en tiempo real. Además la conectividad WIFI y Bluetooth facilita la comunicación inalámbrica con los dispositivos en las bandas. Su tamaño es compacto, ideal para integrarse en nuestro prototipo, manteniendo la estética en el producto y priorizando la comodidad del usuario.
- **Lipo Rider:** Este módulo de carga permite gestionar correctamente la energía entre la batería y el atom ESP32. Ofrece una interconexión de carga USB, esta facilita el recargo sin necesidad de desmontar el dispositivo del pie. Protege contra sobrecargas aumentando así la vida útil de la batería y garantizando que el dispositivo esté listo para cada sesión.
- **Bateria Lipo de 3.7 V 720 mAh:** Esta batería proporciona la energía necesaria para el sistema del dispositivo del pie, ofreciendo estabilidad entre capacidad y tamaño para no afectar la capacidad de uso del dispositivo, por esto es importante controlar el uso, ya que una independencia prolongada es clave para la funcionalidad del dispositivo en la rehabilitación diaria.

### Identificar problemas y realizar mejora antes de la implementación del prototipo

#### Identificación de problemas y recomendaciones de mejora antes de proceder con la implementación del prototipo:

- **Problema 1:** Establecer una conexión en modo esclavo entre el dispositivo Atom y el ESP32. Debemos garantizar un enlace estable y funcional.
- **Problema 2:** Es posible que en el modelo 3D de la sección correspondiente al pie necesite un pequeño cambio que facilite la conectividad del Lipo Rider Plus y el Atom Matrix.
- **Problema 3:** Otra posible área de mejora en el modelo 3D de la sección del pie es el anclaje del interruptor de encendido y apagado. Una revisión en el diseño del anclaje podría proporcionar un mejor ajuste y estabilidad, previniendo movimientos no deseados durante el uso y brindar un acceso más práctico al switch.
- **Problema 4:** Refinar el código actual. Necesitamos garantizar que la medición de los datos en tiempo real por parte del Atom Matrix sea confiable y estable, y de esta manera enviar la información del Atom al ESP32.

**Aspectos a mejorar:** Actualmente, la duración de la batería en modo de uso continuo es de aproximadamente dos horas, lo cual podría ser insuficiente para ciertos escenarios de uso. Para mejorar ello podríamos usar una batería de mayor amperaje para extender la autonomía o, alternativamente, implementar un modo de suspensión en el código que permita reducir el consumo energético cuando el dispositivo no esté en uso activo.

### Identificar retos y limitaciones

<p align="center">
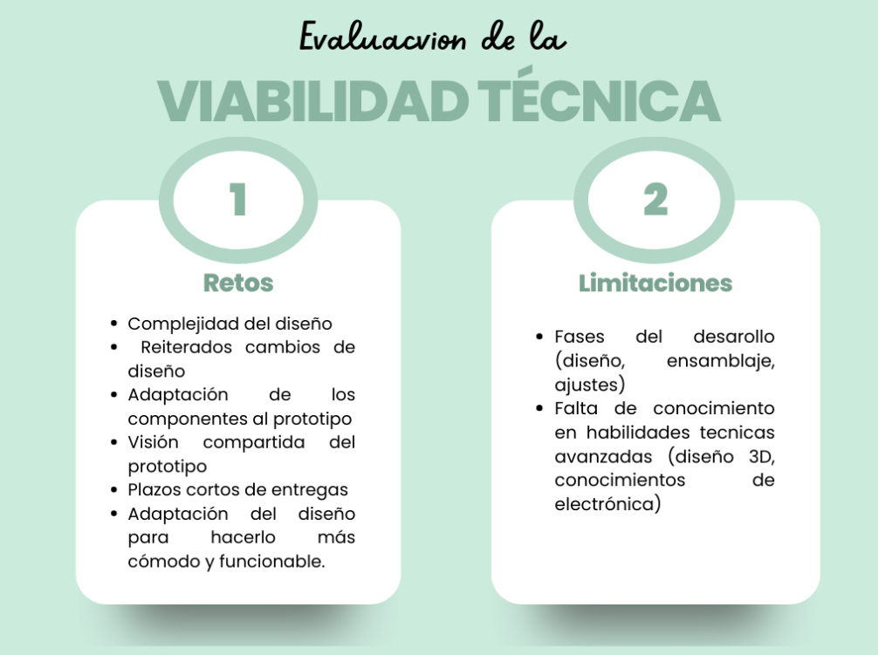
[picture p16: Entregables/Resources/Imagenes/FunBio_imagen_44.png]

</p>

### Propuesta de soluciones

<p align="center">
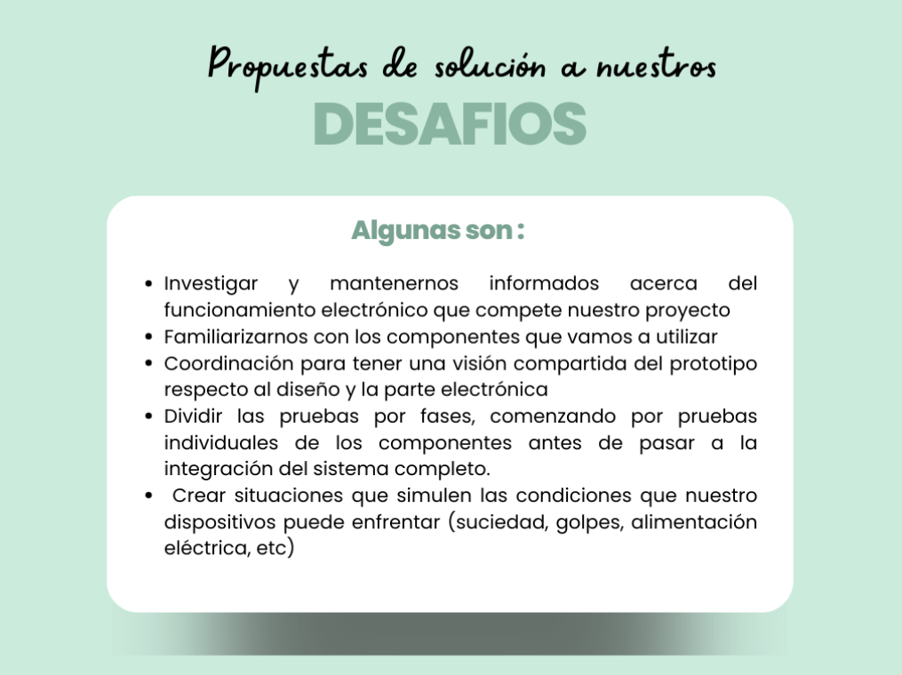
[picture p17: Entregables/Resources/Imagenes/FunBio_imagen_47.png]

</p>

## Avances de esta semana

En esta semana ya se mandaron las piezas a imprimir y con los componentes la pieza se ve asi

<p align="center">
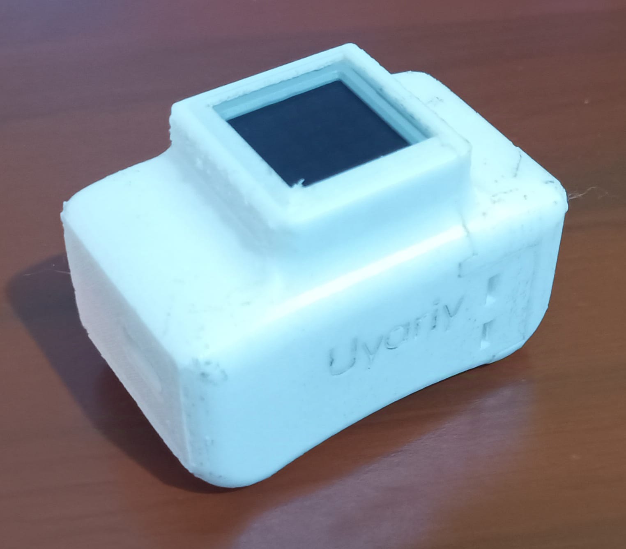
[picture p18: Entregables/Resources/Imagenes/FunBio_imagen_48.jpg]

</p>

Tambien se avanzo con la electronica en la otra pieza del Dispositivo, el video de la prueba se encuentra en el siguiente [link](https://youtu.be/BZDEhf-5Vok)

## Retroalimentación

**- ¿Te parece atractivo el diseño visual del dispositivo?**

Sí, se ve atractivo e innovador para aquellos pacientes con lesión medular con indicación para la marcha. 

**- ¿El tamaño, forma y color del dispositivo parecen adecuados?**

Sí, por todas las sugerencias que se han dado y como se ha estado procediendo con la parte electrónica, está bien la adaptación.

**- ¿Consideras que las partes de contacto con el usuario se ven cómodas?**

No está siendo invasivo para el usuario, puesto que es externo y va en una parte donde el usuario no tiene sensibilidad, por lo cual no incomodaría o afectaría el confort del paciente.

**- ¿La ubicación de los controles parece accesible y fácil de manejar?**

Sí, todo es vía bluetooth.

**- ¿Las funciones del dispositivo son claras?**

Sí,siempre y cuando haya las indicaciones y las preparaciones para el usuario, ello esclarecerá todo para el usuario; las partes técnicas serán brindadas por el terapeuta.

**- ¿Te parece intuitivo el uso del dispositivo según el diseño?**

No, debe de haber una preparación previa.

**- ¿Identificas alguna área en el diseño que podría ser problemática en uso real?**

No se ven áreas del diseño que podrían ser problemáticas; sin embargo, el peor de los casos, es que el usuario no entienda el funcionamiento del dispositivo luego de la explicación.

**- ¿Hay algo que cambiarías en el diseño antes de hacer una versión física?**

El tema del color, por ahora el blanco va bien para mantener la estética y la armonía de colores. Por ahora como prototipo todo está bien.

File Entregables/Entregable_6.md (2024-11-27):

# Iteración y Reporte de Pruebas

## Iteración

### Hardware Electronico

#### Diseño esquemático del circuito

<p align="center">
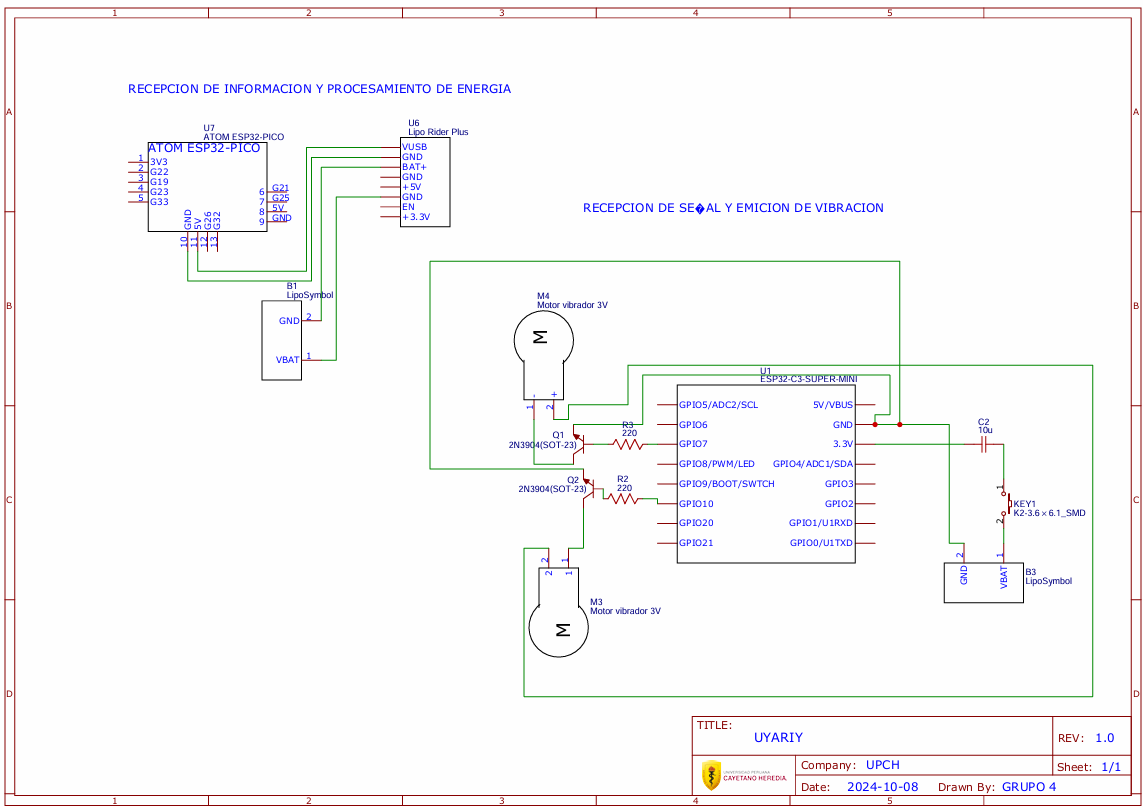
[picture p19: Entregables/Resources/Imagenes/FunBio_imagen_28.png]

</p>

#### Ejecucion del codigo arduino

Para hacer una introduccion al sofware vamos a presentar nuestro **Diagrama de Flujo de Datos** de nuestro codigo

<p align="center">
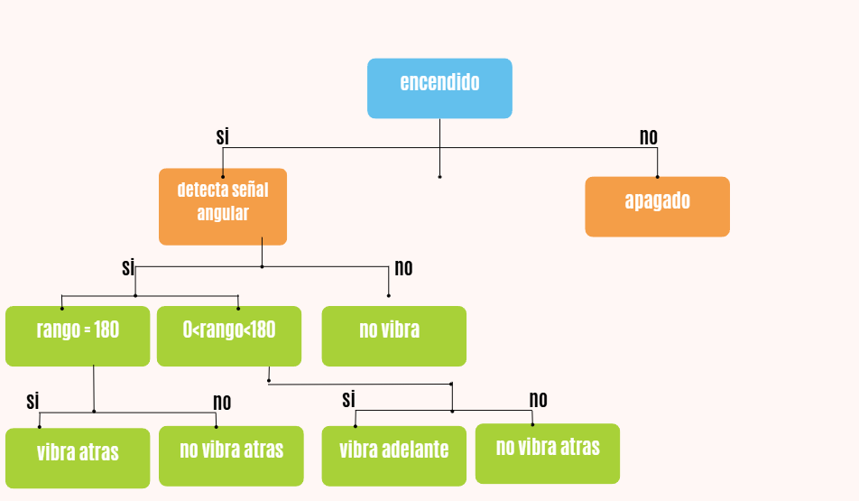
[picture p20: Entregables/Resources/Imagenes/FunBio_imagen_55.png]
DFD

</p>

**Codigo en Arduino para probar los componentes**

<p align="center">
Codigo de Programacion
</p>

#### Prototipado electrónico

<p align="center">
Esquema Electrónico
</p>

### Impresión 3D

#### Modelos 3d Aprobados

- Dispositivo del Pie

<p align="center">
Dispositivo del Pie
</p>

- Dispositivo del Brazo

<p align="center">
Dispositivo del Brazo
</p>

#### Modelado digital del prototipo

- Dispositivo del Pie

<p align="center">
Dispositivo del Pie
</p>

- Dispositivo del Brazo

<p align="center">
Dispositivo del Brazo
</p>

## Reporte de pruebas, retos y limitación de los componentes

### Evaluar funcionalidad y usabilidad por componente

#### Para los componentes que se utilizaran para las bandas en los brazos:

- **Batería de litio:** la batería de litio proporciona la energía necesaria para el sistema, asegurando que la retroalimentación sensorial esté disponible de manera constante. La capacidad debería ser suficiente para mantener el sistema activo durante el tiempo necesario para sesión de rehabilitación sin interrupciones.
- **Lipo Rider Plus:** Este modulo de carga es ideal para facilitar la conexión entre la batería y el sistema EPS 32. Ofrece una interfaz a carga de un puerto USB, asegura una administración de energía eficiente y protege el sistema contra picos de voltaje. Su tamaño es compacto y su diseño modular aumentan la usabilidad, ya que permite que el dispositivo sea recargado fácilmente.
- **Motores vibradores:** Los motores son fundamentales para proporcionar la retroalimentación háptica que el usuario necesita para sentir las pisadas. Colocados estratégicamente en puntos claves de las bandas, pueden dar señales sensoriales claras en función de la presión detectada en los pies. Su respuesta rápida a través de bluetooth al sentir las pisadas además de su bajo consumo de energía los hacen adecuados para este tipo de retroalimentación.
- **ESP32:** este microcontrolador es esencial para procesar los datos del sistema y controlar de manera eficiente el momento de los motores vibradores en tiempo real. Su conectividad WIFI y Bluetooth permite que la comunicación inalámbrica entre nuestro dispositivo y las bandas en los brazos sean efectivas. La flexibilidad y el bajo consumo del ESP32 son ventajas claves, soportan la batería y facilitan el envío y recepción de señales de manera eficiente.

#### Para el dispositivo situado en el pie

- **Atom MPU 6886 ESP32:** Este microcontrolador integrado con un sensor de movimiento (MPU 6886) es fundamental para medir la orientación, aceleración y posibles cambios de posición del pie. Su capacidad para procesar los datos permite una rápida interpretación de los estos para que el sistema proporcione retroalimentación en tiempo real. Además la conectividad WIFI y Bluetooth facilita la comunicación inalámbrica con los dispositivos en las bandas. Su tamaño es compacto, ideal para integrarse en nuestro prototipo, manteniendo la estética en el producto y priorizando la comodidad del usuario.
- **Lipo Rider:** Este módulo de carga permite gestionar correctamente la energía entre la batería y el atom ESP32. Ofrece una interconexión de carga USB, esta facilita el recargo sin necesidad de desmontar el dispositivo del pie. Protege contra sobrecargas aumentando así la vida útil de la batería y garantizando que el dispositivo esté listo para cada sesión.
- **Bateria Lipo de 3.7 V 720 mAh:** Esta batería proporciona la energía necesaria para el sistema del dispositivo del pie, ofreciendo estabilidad entre capacidad y tamaño para no afectar la capacidad de uso del dispositivo, por esto es importante controlar el uso, ya que una independencia prolongada es clave para la funcionalidad del dispositivo en la rehabilitación diaria.

### Identificar problemas y realizar mejora antes de la implementación del prototipo

#### Identificación de problemas y recomendaciones de mejora antes de proceder con la implementación del prototipo:

- **Problema 1:** Establecer una conexión en modo esclavo entre el dispositivo Atom y el ESP32. Debemos garantizar un enlace estable y funcional.
- **Problema 2:** Es posible que en el modelo 3D de la sección correspondiente al pie necesite un pequeño cambio que facilite la conectividad del Lipo Rider Plus y el Atom Matrix.
- **Problema 3:** Otra posible área de mejora en el modelo 3D de la sección del pie es el anclaje del interruptor de encendido y apagado. Una revisión en el diseño del anclaje podría proporcionar un mejor ajuste y estabilidad, previniendo movimientos no deseados durante el uso y brindar un acceso más práctico al switch.
- **Problema 4:** Refinar el código actual. Necesitamos garantizar que la medición de los datos en tiempo real por parte del Atom Matrix sea confiable y estable, y de esta manera enviar la información del Atom al ESP32.

**Aspectos a mejorar:** Actualmente, la duración de la batería en modo de uso continuo es de aproximadamente dos horas, lo cual podría ser insuficiente para ciertos escenarios de uso. Para mejorar ello podríamos usar una batería de mayor amperaje para extender la autonomía o, alternativamente, implementar un modo de suspensión en el código que permita reducir el consumo energético cuando el dispositivo no esté en uso activo.

### Identificar retos y limitaciones

<p align="center">
Identificar retos y limitaciones
</p>

### Propuesta de soluciones

<p align="center">
Identificar retos y limitaciones
</p>

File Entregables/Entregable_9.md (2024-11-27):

# Plan de pruebas de verificación. Pruebas de Verificación del prototipo(video, documentación).

## Verificación de Diseño (Software)

<p align="center">
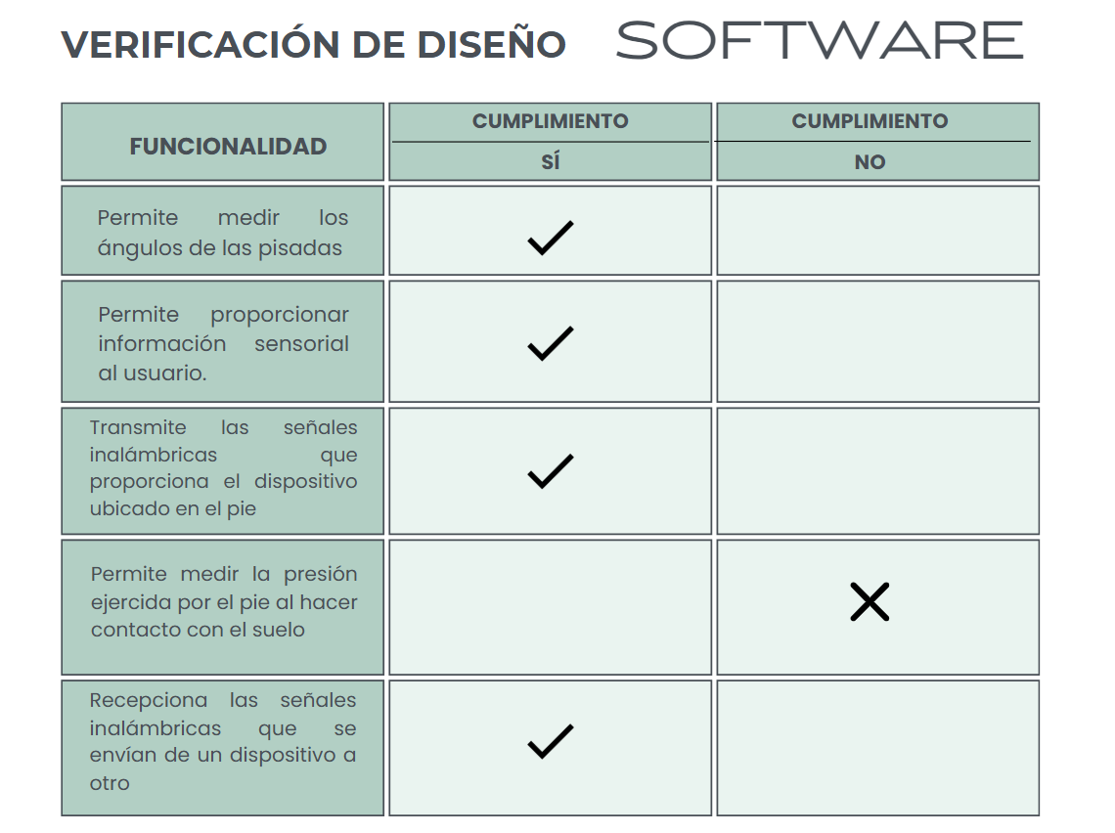
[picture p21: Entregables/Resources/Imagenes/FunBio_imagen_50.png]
Verificación de Diseño (Software)

</p>

## Verificación de Diseño (Hardware)

<p align="center">
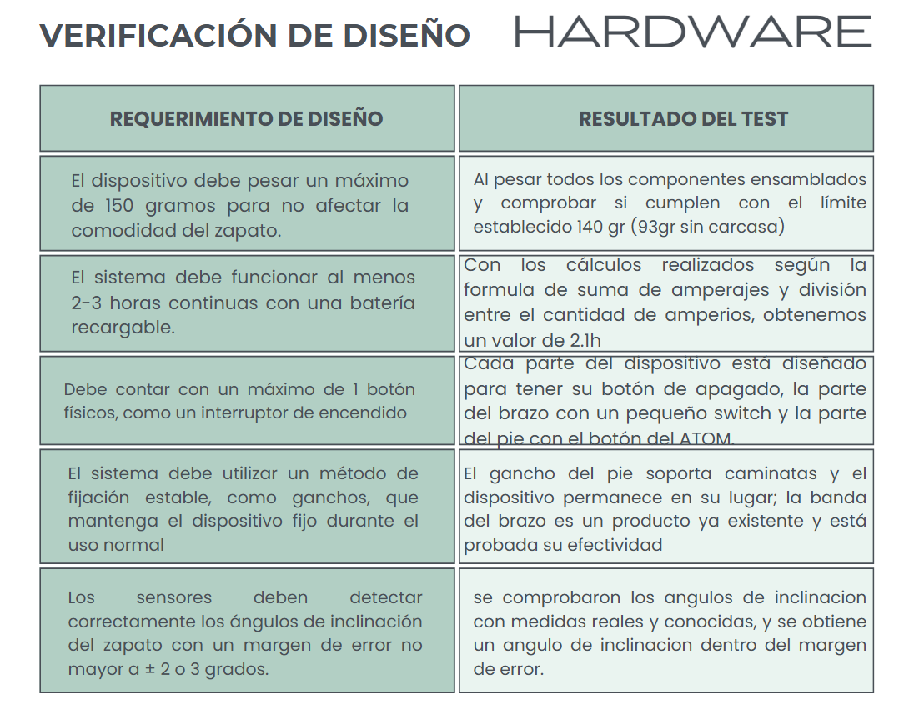
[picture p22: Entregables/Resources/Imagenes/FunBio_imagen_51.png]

</p>

<p align="center">
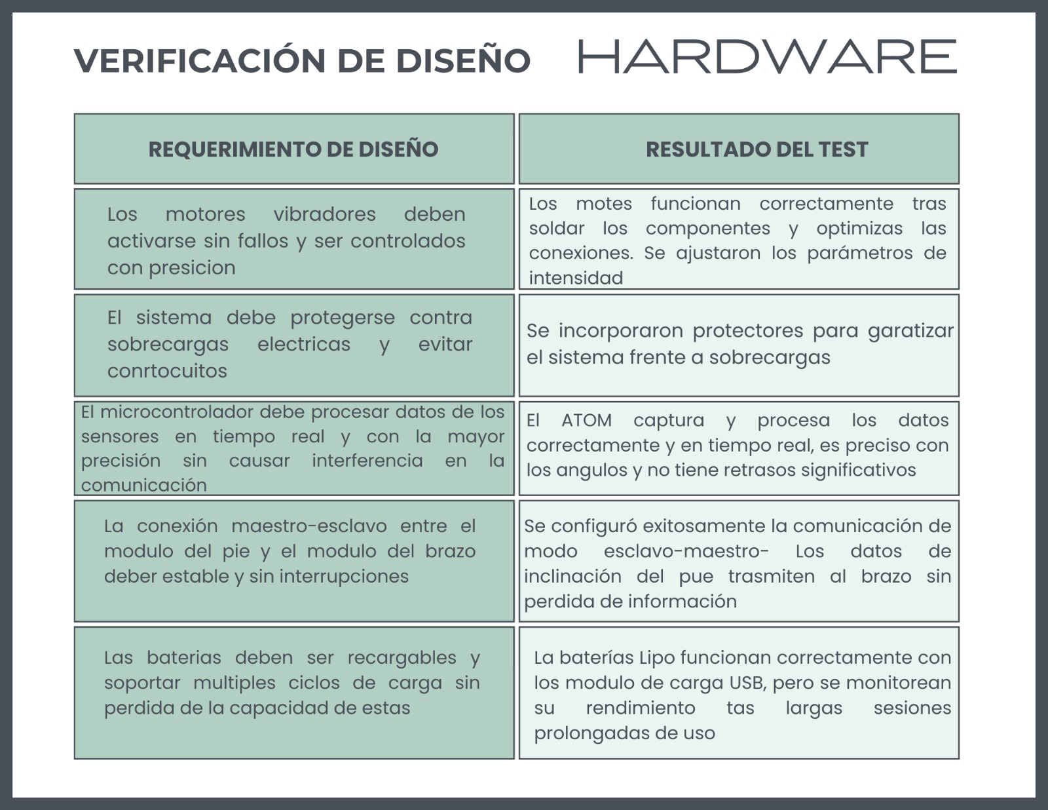
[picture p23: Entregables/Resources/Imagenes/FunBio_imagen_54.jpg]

</p>

<p align="center">
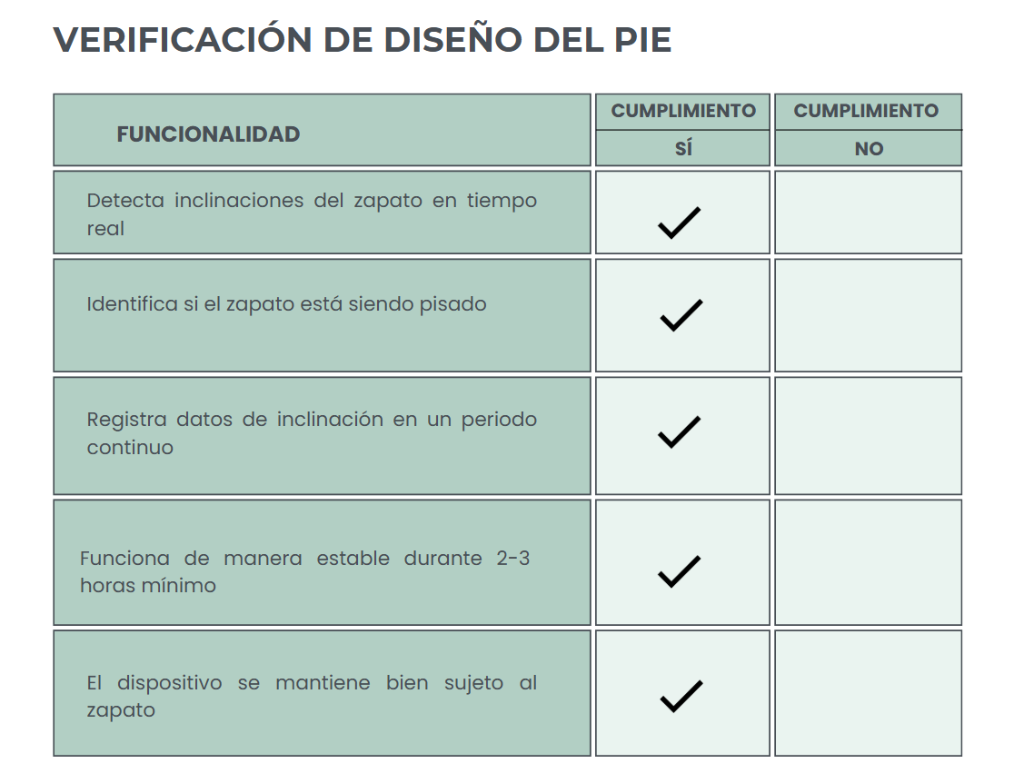
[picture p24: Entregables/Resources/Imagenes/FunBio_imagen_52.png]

</p>

<p align="center">
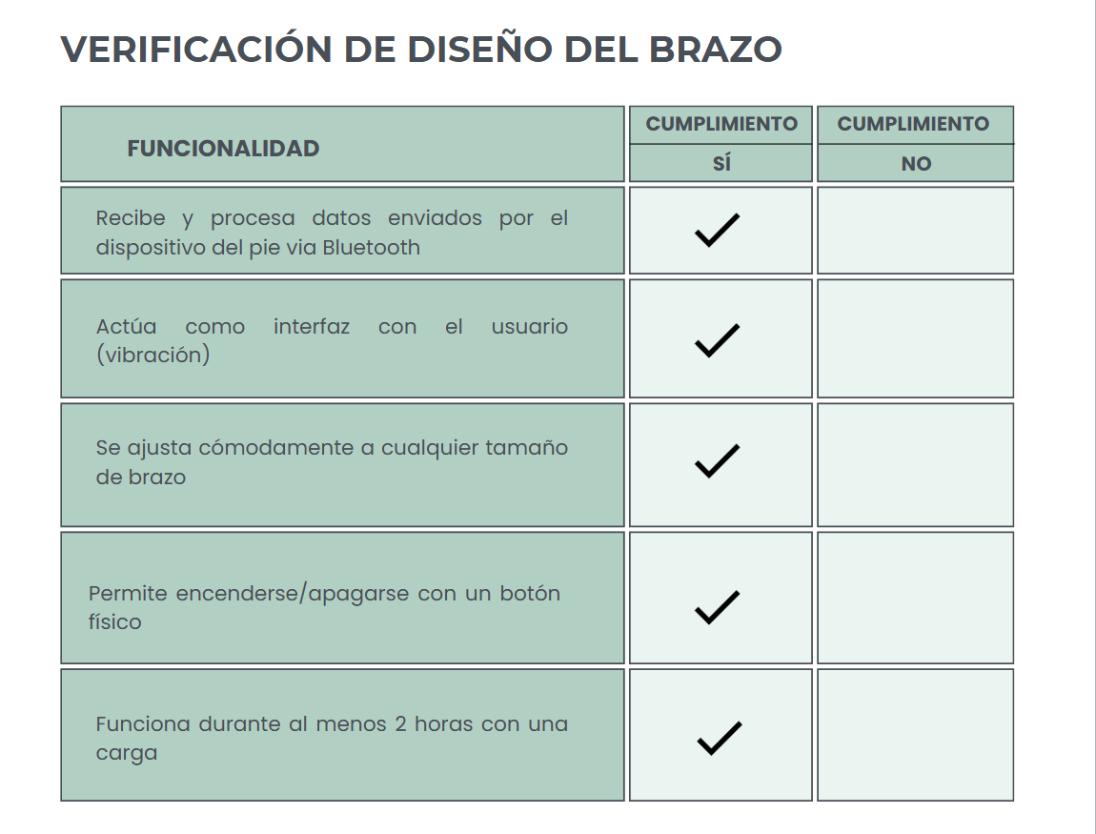
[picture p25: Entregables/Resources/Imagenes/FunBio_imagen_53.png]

</p>

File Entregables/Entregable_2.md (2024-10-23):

# Estado del arte y propuesta de solución

## 1. Contexto comercial

### _Equipo o dispositivo 1:_ Plantilla inteligente para educar posturas al caminar

<p style="line-height: 1.2;">
<strong>Descripción:</strong><br>
Se describe un dispositivo electrónico alimentado por batería, que incluye uno o más sensores de presión en la zona del talón de una plantilla. Estos sensores están conectados a medios de alerta (sensorial, vibrador, luminoso o sonoro) que se activan al detectar la falta de presión adecuada. El dispositivo está protegido por una envoltura que contiene una batería recargable por energía solar, un interruptor y un temporizador para controlar su funcionamiento. Todos los componentes electrónicos se integran en la pieza durante su proceso de fabricación. [1]
</p>
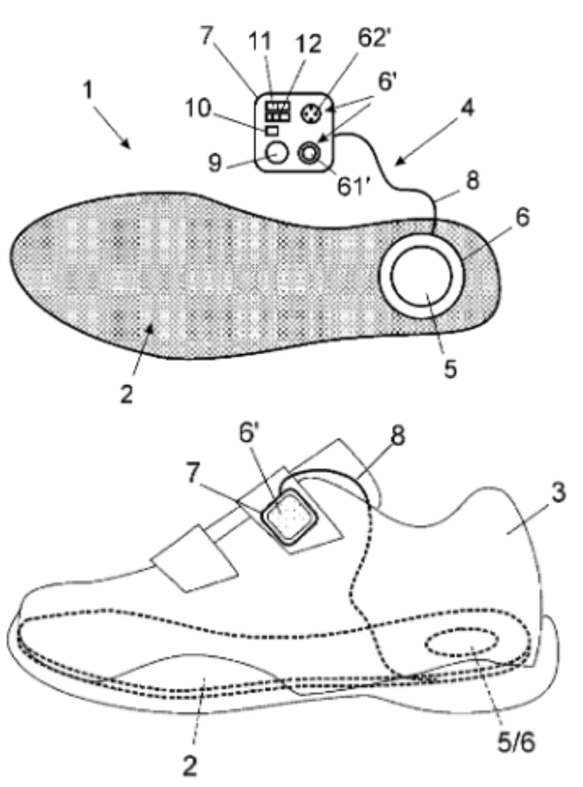
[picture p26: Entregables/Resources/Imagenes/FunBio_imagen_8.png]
Plantilla inteligente para educar posturas al caminar


**_Características_**

<p>- Sensores de presión en el talón<br/>- Medios de alerta conectados a los sensores de tipo sensorial y otro tipo de aviso como sonido o luz<br/>- Alertas luminosas y sonoras que pueden incluir el uso de mensajes pregrabados o música<br/>- Componentes alojados en envoltura independiente, la batería y medios de alerta están protegidos en una envoltura que fijarse al zapato<br/>- Conexión inalámbrica o cableada<br/>- Alimentación por batería recargable , tiene opción de recarga solar<br/>- Control y ajuste del sistema, tiene un interruptor de encendido/apagado, un temporizador y control del volumen para las alertas sonoras</p>

Fuente: https://patentscope.wipo.int/search/es/detail.jsf?docId=WO2016181002&_cid=P20-M14HPI-62809-1
<br/>

### _Equipo o dispositivo 2:_ Calzado que incluye una construcción durable de combinación

<p style="line-height: 1.2;">
<strong>Descripción:</strong><br>
El producto es una calzado diseñado para mejorar la sensibilidad al caminar, que permite al usuario sentir los contornos del terreno a través de ella, proporcionado una retroalimentación propioceptiva mejorada. Este diseño permite que el usuario perciba movimientos de la suela y el suelo con mayor precisión, mejorando la comodidad y el control al caminar, mejorando la propiocepción. [2]
</p>
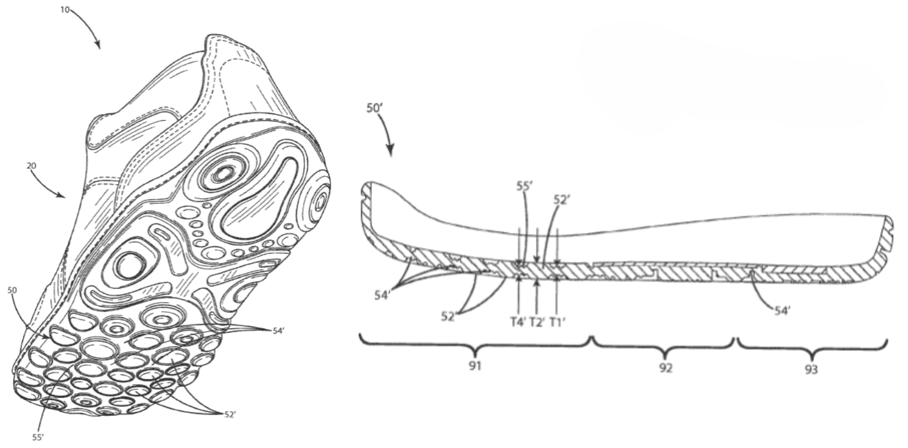
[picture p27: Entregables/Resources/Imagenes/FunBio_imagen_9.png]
Calzado que incluye una construcción durable de combinación


**_Características_**

<p>- Contiene un corte con un forro interior, cuya parte inferior está sellada con un cierre que contiene un núcleo de espuma con memoria<br/>- Un tablero Strobel flexible, que contribuye a la flexibilidad del calzado<br/>- Una suela flexible y maleable que permite al usuario sentir los contornos del terreno</p>

<br/>
Fuente: https://patents.google.com/patent/ES2715856T3/

### _Equipo o dispositivo 3:_ Walkasins by RxFunction

<p style="line-height: 1.2;">
<strong>Descripción:</strong><br>
Walkasins es una prótesis sensorial portátil diseñada primordialmente para personas con neuropatía sensorial periférica que han perdido la sensibilidad en los pies, lo que afecta su equilibrio y aumenta el riesgo de caídas. El dispositivo funciona detectando la presión en la planta del pie mediante un sensor colocado en la plantilla. Esta información es enviada a una distancia cercana como es el tobillo y transforma esta señal en estímulos. Esos estímulos se transmiten en tiempo real a diferentes áreas de la pierna (delantera, trasera, izquierda y derecha), donde la sensibilidad de la piel todavía está presente. Esta retroalimentación vibratoria permite que el cerebro integre la nueva información sensorial, compensando la pérdida de sensación en la planta del pie. Como resultado, el usuario obtiene un mejor control de la postura y el equilibrio, lo que reduce que el paciente camine de manera inestable y pueda ocasionar caídas. [3]
</p>
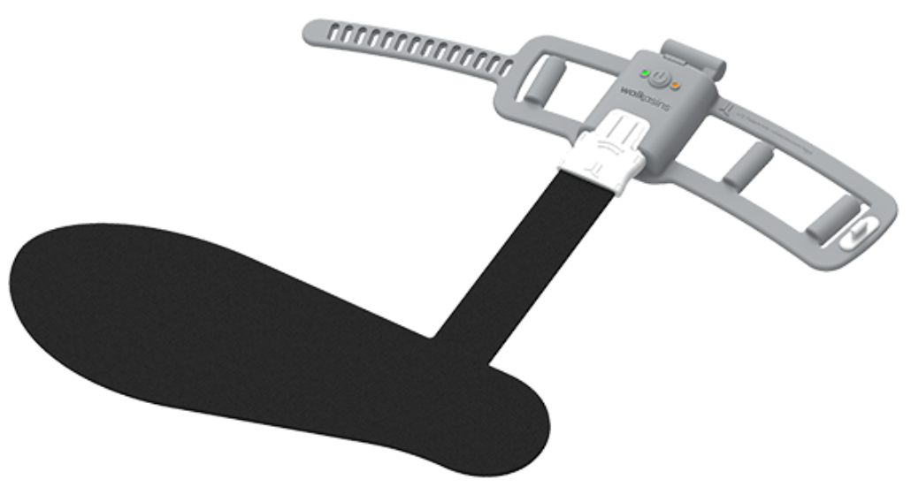
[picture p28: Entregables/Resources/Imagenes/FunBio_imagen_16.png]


**_Características_**

<p><strong>Tipo:</strong> Dispositivo recetado para uso diario.<br/><strong>Sensor:</strong> Mide la presión en la plantilla del pie.<br/><strong>Unidad:</strong> Colocada en el tobillo.<br/><strong>Estímulo:</strong> Vibraciones táctiles direccionales en tiempo real.<br/><strong>Propósito:</strong> Mejora el equilibrio y la marcha.<br/><strong>Pruebas:</strong> Clínicamente comprobado para reducir caídas.<br/><strong>Diseño:</strong> No invasivo, para uso a largo plazo.<br/></p>

<p align="center">
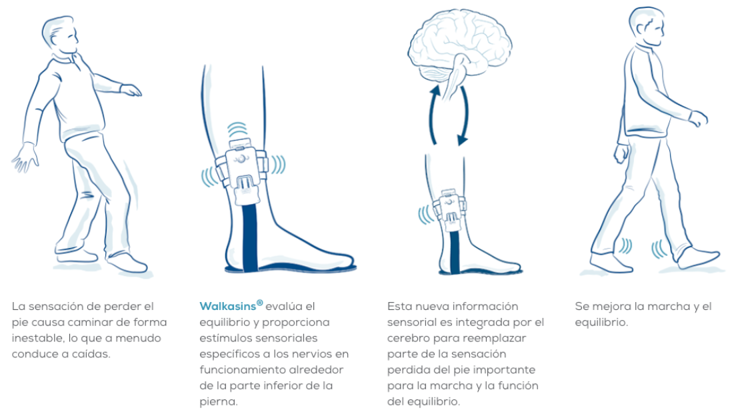
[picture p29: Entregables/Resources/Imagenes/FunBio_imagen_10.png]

</p>

Fuente: https://rxfunction.com/our-product/

### Patente 1 (Invención)

| **AU2019264535 (B2) - Mobility aid** |
|-----------------------------------------------------------------------------|
| **Inventor (es) :** Pape, Lise S.<br/>**Procedencia :** Australia<br/>**Año:** 2019 |
| AU2019264535 (B2)<br/><br/><br/>La presente invención proporciona un sistema para ayudar a un usuario a moverse, que comprende un sensor  configurado para detectar un parámetro que indica una posición del pie del usuario; La presente invención es beneficiosa porque aumenta la confianza y/o eficiencia en el movimiento, proporcionando ayudas visuales y/o táctiles para guiar al usuario. [[4]](https://github.com/Misancio-T/FUNBIO---GRUPO-4/blob/main/Entregables/Entregable_2.md#4-bibliograf%C3%ADa)<br/><br/><br/>Fuente: https://patents.google.com/patent/AU2019264535B2/ |

### Patente 2 (Invención)

| **EP2729096 (B1) - Sistemas, dispositivos y métodos para monitorear el perfil de carga bajo los pies de un paciente durante un período de carga parcial de peso** |
|-----------------------------------------------------------------------------|
| **Inventor (es) :** Kubiak, Erik N; North, Kylee; Hitchcock, Robert W.<br/>**Procedencia :** Alemania<br/>**Año:** 2011 |
| EP2729096 (B1)<br/><br/><br/>La presente divulgación se refiere en general a sistemas, dispositivos y métodos para medir perfiles de carga bajo el pie. Más particularmente, la divulgación se refiere a sistemas, dispositivos y métodos para monitorear un perfil de carga bajo el pie de un paciente con fractura durante un período de carga parcial de peso (PWB). [[5]](https://github.com/Misancio-T/FUNBIO---GRUPO-4/blob/main/Entregables/Entregable_2.md#4-bibliograf%C3%ADa)<br/><br/><br/>Fuente: https://patents.google.com/patent/EP2729096B1/ |

### Patente 3 (Invención)

| **US7771371 (B2) - Sports shoe with sensing and control** |
|-----------------------------------------------------------------------------|
| **Inventor (es) :** Avni, Arik<br/>**Procedencia :** Estados Unidos<br/>**Año:** 2010 |
| US7771371 (B2)<br/>La patente describe un dispositivo para mejorar el rendimiento atlético del usuario, que consta de una plantilla flexible diseñada para insertarse en un zapato y equipada con una o más cámaras internas. Este dispositivo incluye un estimulador y una unidad de control que detecta las presiones en las cámaras y dirige el estimulador para proporcionar retroalimentación en función de las presiones detectadas y los parámetros deseados del rendimiento atlético. La plantilla incorpora sensores de presión o fuerza para medir la carga aplicada al pie durante la actividad física, y el estimulador puede ofrecer retroalimentación auditiva, táctil o visual. El sistema permite el monitoreo en tiempo real del peso soportado y utiliza estimulación cerrada para mejorar el rendimiento atlético. Además, la unidad de control puede tener una interfaz con una pantalla que muestra un número limitado de parámetros útiles para los entrenadores deportivos, evitando categorías adicionales que no sean prácticas para el entrenamiento. [[6]](https://github.com/Misancio-T/FUNBIO---GRUPO-4/blob/main/Entregables/Entregable_2.md#4-bibliograf%C3%ADa)<br/><br/><br/>Fuente: https://patents.google.com/patent/US7771371B2/ |

### Patente 4 (Utilidad)

| **US10809804 (B2) - Wearable Haptic Feedback Glove** |
|-----------------------------------------------------------------------------|
| **Inventor (es) :** Goupil, Marc. Y; Rojanachaichanin, Bodin L; Sjoberg, Kurt C; Piller, Paul; Bonafede, Nicholas J; Jr; Takatsuka, Ryan M.<br/>**Procedencia :** Estados Unidos<br/>**Año:** 2020 |
| US10809804 (B2)<br/>La patente describe un guante de retroalimentación háptica diseñado para mejorar la interacción con entornos virtuales y dispositivos robóticos. Este guante está hecho de un material flexible y cuenta con dedales en cada dedo y pulgar, así como tendones acoplados a estos dedales. Los tendones están conectados a actuadores que aplican presión a los dedos para proporcionar una sensación táctil. Además, el guante incluye tactores tanto en los dedales como en los paneles de la palma para ofrecer retroalimentación háptica adicional. La patente aborda la necesidad de sistemas de retroalimentación háptica que sean menos voluminosos, más sensibles e interactivos que los existentes. [[7]](https://github.com/Misancio-T/FUNBIO---GRUPO-4/blob/main/Entregables/Entregable_2.md#4-bibliograf%C3%ADa)<br/><br/><br/>Fuente: https://patents.google.com/patent/US10809804B2/ |

## 2. Lista de requerimientos

**Funcionales**
<p align="center">
EasyStand Evolve
</p>

**No Funcionales**
<p align="center">
EasyStand Evolve
</p>

## 3. Propuesta de solución

**Dispositivo con deteccion de movimiento + Banda de vibración**
- Dispositivo enfocado en la traslado inalambrico de la sensación háptica durante las fases de la marcha hacia los brazos, donde se percibe mediante vibraciones. El dispositivo se utilizaria principalmente en rehabilitación. (Lesión medular tipo A)

## 4. Bibliografía

- [1] Gutierrez Perez, Paula Manuela. Plantilla inteligente para educar posturas al caminar. 2016. https://patentscope.wipo.int/search/es/detail.jsf?docId=WO2016181002&_cid=P20-M14HPI-62809-1
- [2] Ruiz, N. D., Loverin, M. R., & Inc, W. O. (2014, 14 marzo). ES2715856T3 - Calzado que incluye una construcción durable de combinación. https://patents.google.com/patent/ES2715856T3/
- [3] RxFunction. (2023, 8 marzo). About Walkasins. A peripheral neuropathy device. https://rxfunction.com/our-product/
- [4] Pape, L. S., & Individual. (2014, 14 junio). AU2019264535B2 - Mobility aid. https://patents.google.com/patent/AU2019264535B2/
- [5] Kubiak, E. N., North, K., & Hitchcock, R. W. (2011, 7 julio). EP2729096B1 - Systems, devices, and methods for monitoring an under foot load profile of a patient during a period of partial weight bearing. https://patents.google.com/patent/EP2729096B1/
- [6] Arik Avni, Meitar (IL). Sports shoe with sensing and control. 2010. https://patents.google.com/patent/US7771371B2/
- [7] Marc Y. Goupil ; Bodin L. Rojanachaichanin; Kurt C. Sjoberg; Paul Piller ; Nicholas J. Bonafede ; Ryan M. Takatsuka. Haptic feedback glove. 2020. https://patents.google.com/patent/US10809804B2

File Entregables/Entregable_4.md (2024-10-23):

# Análisis de la propuesta de solución

## Caja negra (Lista de entradas y salidas)

<p align="center">
Caja Negra
</p>

## Esquema de funciones

<p align="center">
Esquema de funciones
</p>

## Matriz morfológica

<p align="center">
Matriz morfológica
</p>

## Tabla de valoración

<p align="center">
Tabla de valoración
</p>

## Mas informacion acerca del Atom Matrix

<p align="center">
Atom Matrix
</p>

## Conclusión del concepto de solución elegido

La propuesta número **4** fue la ganadora por su acceso relativamente accesible y la efectividad de su uso. Ya que los componentes seleccionados se comunican sin necesidad de cables, haciendo cómodo y adaptable a su uso en las zapatillas. Además de su rapidez en las notificaciones del sensor de presión y su fácil uso de los pacientes.

## Bocetos

### En el dispositivo del zapato

<p align="center">
Plantilla lateral
</p>

### En la banda de los brazos

<p align="center">
Brazos
</p>

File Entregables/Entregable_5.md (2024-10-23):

# Esquema Electrónico y Modelado 3D

## Diagrama o Esquema Electrónico del concepto de solución

<p align="center">
Esquema Electrónico
</p>

## Modelado 3D de los componentes del concepto de la solución

### Banda en el brazo

#### Diseños Importados

**Batería de Litio**

<p align="center">
Batería de Litio
</p>

**LiPo Rider Plus**

<p align="center">
LiPo Rider Plus
</p>

**ESP-32**

<p align="center">
ESP-32
</p>

**Motor de vibracion**

<p align="center">
Motor de vibracion
</p>

#### Diseños Modelados

**Parte Frontal**

<p align="center">
Vista Frontal
</p>

**Parte Trasera**

<p align="center">
LiPo Rider Plus
</p>

**Parte Intermedia**

<p align="center">
ESP-32
</p>

### Artefacto en el Zapato

#### Diseños Modelados

**Parte Frontal**

<p align="center">
Vista Frontal 2
</p>

**Diseño Interno**

<p align="center">
LiPo Rider Plus 2
</p>

**Parte Trasera**

<p align="center">
ESP-32 2
</p>

### Links de los Diseños

- https://sketchfab.com/misaeltorresbautista/models
- https://sketchfab.com/WilliamUPCH/models

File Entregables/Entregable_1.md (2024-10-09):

# Análisis del Caso

## 1. Definiciones de términos clave
- **Lesión de médula espinal (LME):** Trauma o daño de la médula espinal que tiene como resultado la pérdida de algunas funciones motoras y/o sensoriales; estas pueden ser totales o parciales.
- **Lesión medular completa:** Pérdida total de las funciones motoras y sensoriales por debajo del nivel de la lesión.
- **Autonomía vesical y gastrointestinal:** Capacidad del paciente en controlar las funciones de la vejiga e intestino que podría verse afectada por la lesión de médula espinal, dependiendo el nivel y gravedad de la lesión.
- **Paraplejia:** Parálisis parcial o completa de las extremidades inferiores y parte del tronco, con pérdida de funciones sensoriales y motoras por debajo del nivel de la lesión.
- **Rehabilitación en lesiones medulares:** Incluye actividades como exámenes de laboratorio, estudios de imágenes, terapias físicas, medidas de prevención, dispositivos, tratamiento farmacológico, evaluaciones psicológicas y psiquiátricas, entre otra.
- **Apoyo psicosocial:** En el contexto de lesiones medulares, hace referencia al soporte emocional y social que recibe el paciente y su familia, lo cual es crucial para la calidad de vida.

## 2. Desarrollo de la temática
Los daños producidos en la médula espinal por traumatismos (caídas y accidentes de tráfico) o por causas no traumáticas, como tumores, enfermedades degenerativas y vasculares, infecciones, toxinas o defectos congénitos son definidos como una lesión medular [[1]](https://github.com/Misancio-T/FUNBIO---GRUPO-4/blob/main/Entregables/Entregable_1.md#8-bibliograf%C3%ADa).  Este hecho se concreta en la pérdida del movimiento voluntario, de la sensibilidad, además se producen trastornos neurovegetativos, alteraciones de las funciones vesical e intestinal, del sistema cardiovascular, de la función sexual, entre otras complicaciones [[2]](https://github.com/Misancio-T/FUNBIO---GRUPO-4/blob/main/Entregables/Entregable_1.md#8-bibliograf%C3%ADa). El grado de deterioro relacionado con una lesión medular depende de la gravedad de la lesión y de su localización en la médula espinal. La lesión medular provoca la pérdida completa o incompleta de las funciones sensoriales y/o motoras por debajo del nivel de la lesión [[1]](https://github.com/Misancio-T/FUNBIO---GRUPO-4/blob/main/Entregables/Entregable_1.md#8-bibliograf%C3%ADa). Las lesiones de la médula espinal pueden afectar la capacidad para realizar actividades de la vida diaria, como caminar, utilizar los brazos, vaciar fisiológicamente el intestino o la vejiga, o lavarse y vestirse. Estas limitaciones se ven agravadas por, actitudes negativas y barreras físicas a la movilidad básica que limitan la independencia y la plena participación social, lo cual a corto plazo genera fuertes sentimientos de tristeza, culpa o inutilidad, este es motivo por el cual muchos llevan tratamientos psicológicos para poder afrontar su situación de la mejor manera. El paciente del caso clínico que se nos otorgó cuenta con una lesión medular de grado tipo A completa que comprende las zonas D10 a L2, teniendo una factura D11 - D12. 

En la zona dorsal, de la D10 A D12, encontramos vértebras que forman parte de la columna torácica inferior , en este nivel, las lesiones pueden afectar las funciones del tronco y los músculos que ayudan a tener una correcta respiración. En la zona lumbar, de la L1 a L2, se encuentran las raíces de los nervios que transmiten sensibilidad y acción motora hacia y desde los miembros inferiores del cuerpo, también las afecciones en esta zona pueden desfavorecer el control de las funciones intestinales y vesicales del paciente.

## 3. Contexto nacional 
En nuestro país no hay estudios de incidencia, ni prevalencia de lesión medular, ni tampoco es posible estimar estos datos por no contar con data estandarizada ni con un sistema informático adecuado para realizar el reporte respectivo. Por lo cual se ha tornado en cuenta sólo fue reportado por el sistema informático del instituto Nacional de Rehabilitación “Dra. Adriana Rebaza Flores" AMISTAD PERÚ-JAPÓN, durante los años del 2012 al 2018 el Departamento de investigación, Docencia y Rehabilitación Integral en Lesiones Medulares ha atendido aproximadamente 1800 pacientes con lesión medular nuevos en consulta externa, y por año aproximadamente se ha atendido 260 pacientes nuevos (Io que equivale a 19% en promedio de las atenciones en este departamento), durante el periodo 2012 - 2018 el 45% de casos atendidos corresponden a causas traumáticas, el 43% a las no traumáticas, el 8% a las secuelas de poliomielitis. Asimismo, del 2014 al 2017 las causas de lesiones traumáticas se dividen en: 38% por accidentes de tránsito, 35% ocasionadas por caídas, y el 17% debido a lesiones de armas; porcentajes similares a los reportados por otros países (Estados Unidos) [[4]](https://github.com/Misancio-T/FUNBIO---GRUPO-4/blob/main/Entregables/Entregable_1.md#8-bibliograf%C3%ADa).

El sistema de diagnóstico y tratamiento que se realizan en nuestro país es clásico y tiene como objetivo disminuir la morbilidad y mortalidad derivada de las lesiones medulares, para esto se realizan un proceso de actividades como: Solicitar exámenes de laboratorio, estudios de imágenes; interconsultas; terapias físicas; instaurar medidas de prevención y dispositivos (camas especializadas, sillas, cojines); tratamiento farmacológico; orientación y consejos sobre sexualidad, fertilidad y gestación;  evaluaciones conductuales, psicológicas y psiquiátricas; etc.

Para clasificar a cada paciente, nuestros centros de rehabilitación siguen los Estándares Internacionales para la Clasificación Neurológica de la Lesión de la Médula Espinal (ISNCSCI), lo cual nos permite hacer un mejor enfoque en las zonas con repercusiones.

<p style="line-height: 1.2;">
<strong>Figura 1</strong><br>
Internacional Standards for Neurological Classification of SCI (ISNCSCI) Worksheet
</p>
<p align="center">
  Descripción de la imagen
</p>
<p style="line/height: 1;">
Extraido de: https://asia-spinalinjury.org/international-standards-neurological-classification-sci-isncsci-worksheet/
</p>

En el aspecto de hospitalización, nuestro protocolo se basa en evaluar el grado de lesión que tiene el paciente y asignarle un tratamiento adecuado que depende de cada caso presentado en el Instituto Nacional de Rehabilitación; algunas de las prácticas que se hacen en el área de hospitalización son: Aplicar técnicas atraumáticas de inserción de catéter; retirar SVP prontamente y reeducar las vías urinarias, si no hay contraindicaciones; cuidados de la piel y cambios posturales activos o pasivos; seguimiento de un plan nutricional especial para cada paciente y manejo conjunto para entrenamiento en movilizaciones y/o transferencias mediante técnicas seguras con apoyos técnicos y/o asistencia requerida según funcionalidad, asimismo, entrenamiento de técnicas de caídas y reincorporación a la silla de ruedas.

Según la Revista Médica Herediana, las revisiones sobre la repercusión de la lesión medular hacen referencia de lo complejo que resulta para una persona portadora de una lesión medular y su familia convivir con esta condición. Los aspectos psicosociales, especialmente el apoyo social, son tan importantes como los aspectos clínicos cuando se habla de la calidad de vida en las personas que presentan una lesión medular espinal (LME). Sin embargo, cabe mencionar que se han encontrado pocos estudios sobre la repercusión familiar y apoyo social en las familias de personas con lesión medular, la mayoría de estudios estuvieron relacionados a la discapacidad como tema general. La población de estudio observada a continuación estuvo conformada por todos los familiares de pacientes con LME que se encontraron hospitalizados y recibieron tratamiento de rehabilitación desde Septiembre a diciembre del 2019 [[5]](https://github.com/Misancio-T/FUNBIO---GRUPO-4/blob/main/Entregables/Entregable_1.md#8-bibliograf%C3%ADa).

<p style="line-height: 1.2;">
<strong>Tabla 1</strong><br>
Características generales del paciente con lesión medular 
</p>
<p align="center">
  Descripción de la imagen
</p>
<p style="line/height: 1;">
Extraido de: https://doi.org/10.20453/rmh.v33i2.4243
</p>

<p style="line-height: 1.2;">
<strong>Tabla 2</strong><br>
Repercusión familiar por áreas y global en pacientes con lesión medular 
</p>
<p align="center">
  Descripción de la imagen
</p>
<p style="line/height: 1;">
Extraido de: https://doi.org/10.20453/rmh.v33i2.4243
</p>

Se encontró que los pacientes de 18 a más años tienen menos prevalencia de repercusión familiar severa que los pacientes que tienen de 12 a 17 años, lo que podría explicarse porque en los adolescentes se acentúan los cambios que presentan en su cuerpo y corporalidad en el cambio de la imagen de sí mismo, las relaciones contradictorias   principalmente   con   su   familia   y   amigos, la carga de la discapacidad y el proceso de adaptación a su condición. También, el 44% de los pacientes y el 58% de los familiares tenían entre 30 y 59 años. El 34% de los cuidadores eran cónyuges del paciente, el 48% era familia de tipo nuclear y el 62% de las familias pertenecieron al nivel socioeconómico de pobreza extrema. El 78% de los pacientes tenían paraplejía y el 48% lesión tipo ASIA A. La repercusión global, fue elevada en 68% y con un sentido negativo en 94% de los casos [[5]](https://github.com/Misancio-T/FUNBIO---GRUPO-4/blob/main/Entregables/Entregable_1.md#8-bibliograf%C3%ADa).   

Los resultados de esta investigación se deben interpretar con cautela, primero, no se tuvo el poder estadístico suficiente para encontrar la asociación entre el apoyo social y la repercusión familiar ya que no se calculó tamaño de muestra porque no se encontraron datos de otras investigaciones que sean de utilidad para dicho cálculo, por lo que, solo se evaluaron a todos los familiares de los pacientes con lesión medular que cumplan los criterios de selección en un periodo de tres meses. Segundo, el apoyo social y repercusión familiar podría variar dependiendo del nivel de atención, categorización y ubicación de la institución prestadora de servicios de salud en los que los pacientes y familiares se atienden; incluso si éstos no están institucionalizados [[5]](https://github.com/Misancio-T/FUNBIO---GRUPO-4/blob/main/Entregables/Entregable_1.md#8-bibliograf%C3%ADa).

A continuación, presentaremos una tabla acerca de nuestro paciente, englobando la prevención, diagnóstico, tratamiento y monitoreo de este.
<br/>
<p style="line-height: 1.2;">
<strong>Tabla 3</strong><br>
Profundizando en el caso del paciente
</p>
<p align="center">

| **Prevención** | **Diagnóstico** | **Tratamiento** | **Monitoreo** |
| ---------- | ----------- | ----------- | --------- |
| Las lesiones medulares se pueden producir de distintas maneras, la mayor parte de ellas por accidentes. Aunque un accidente no se puede evitar, es importante que se tenga un instinto de supervivencia para evaluar por nuestra cuenta donde es posible estar parado para tener la menor probabilidad de sufrir un accidente. Luego de sufrir un accidente que pueda derivar en una lesión medular o observar algún caso, lo primero que debemos hacer es llamar a una ambulancia para un rápido diagnóstico y evitar más problemas. | La lesión se produjo debido a la caída del paciente desde un segundo piso, donde luego del golpe quedó inconsciente. El paciente presenta una lesión por fractura en D11-D12. La lesión es completa, presenta movimiento activo en los miembros superiores pero en los miembros inferiores es ausente. Debido a la lesión el paciente presenta sensación de llenado de la uretra pero no es capaz de relajar los músculos para dejar salir la orina. Adicionalmente no presenta actividad sexual. | Actualmente el paciente se encuentra en el Instituto Nacional de Rehabilitación, donde debido a su problema en la vejiga usa una sonda Foley para la extracción de esta. El paciente usa silla de ruedas para desplazarse por el entorno y gracias a su movilidad activa en los miembros superiores presenta cierta independencia. Aunque no presenta movilidad en los miembros inferiores, el paciente en ocasiones con ayuda cambia su cuerpo de posición  para evitar posibles daños por estar siempre sentado. | Tanto para nuestro paciente como para otros pacientes que presentan la misma lesión por fractura en D11-D12 luego de su tratamiento no obtienen gran monitoreo, la capacidad de poder utilizar sus miembros superiores les da independencia al menos mientras están sobre la silla de ruedas. Un monitoreo importante es estar atento con la sonda Foley, para cambiarla si es necesario y colocarla correctamente para evitar problemas. |

</p>
<p style="line/height: 1;">
Extraido de: Elaboración propia
</p>

## 4. Contexto mundial 
A nivel mundial, las lesiones medulares (SCI)  son una de las principales causas de discapacidad de larga duración, las estimaciones indican que aproximadamente 15,4 millones de personas tenían una lesión en la médula espinal en 2021 [1] .Las estadísticas que muestra el Centro Nacional de Estadística sobre Lesiones de la Médula Espinal (NSCISC) indican lo siguiente:
Los accidentes automovilísticos son la principal causa de lesiones más reciente, seguidos de cerca por las caídas. Los actos de violencia (en primer lugar, las heridas de bala) y las actividades deportivas/recreativas también son causas relativamente frecuentes  [[3]](https://github.com/Misancio-T/FUNBIO---GRUPO-4/blob/main/Entregables/Entregable_1.md#8-bibliograf%C3%ADa).

<p style="line-height: 1.2;">
<strong>Figura 2</strong><br>
Estadisticas de las causas de lesiones medulares 
</p>
<p align="center">
  Descripción de la imagen
</p>
<p style="line/height: 1;">
Extraido de: https://msktc.org/sites/default/files/FactsFigures2021-Spanish-508.pdf
</p>

A nivel neurológico y magnitud de lesión la tetraplejia incompleta es la categoría neurológica más frecuente. La frecuencia de la paraplejia incompleta y la completa es prácticamente la misma. Menos del 1 % de las personas tuvieron una recuperación neurológica completa para cuando recibieron el alta médica  [[3]](https://github.com/Misancio-T/FUNBIO---GRUPO-4/blob/main/Entregables/Entregable_1.md#8-bibliograf%C3%ADa).

<p style="line-height: 1.2;">
<strong>Figura 3</strong><br>
Estadisticas de la magnitud de la lesión en lesiones medulares 
</p>
<p align="center">
  Descripción de la imagen
</p>
<p style="line/height: 1;">
Extraido de: https://msktc.org/sites/default/files/FactsFigures2021-Spanish-508.pdf
</p>

También, observamos que el promedio de esperanza de vida de las personas con SCI no ha mejorado desde la década de 1980 al 2015 y sigue estando muy por debajo de la esperanza de vida de las personas sin SCI. Los índices de mortalidad son considerablemente más altos durante el primer año después de la lesión que en los años siguientes, sobre todo en el caso de las personas con un deterioro neurológico más grave [[3]](https://github.com/Misancio-T/FUNBIO---GRUPO-4/blob/main/Entregables/Entregable_1.md#8-bibliograf%C3%ADa).

<p style="line-height: 1.2;">
<strong>Tabla 4</strong><br>
Esperanza de vida (años) después de la lesión según la gravedad de la lesión y la edad al lesionarse 
</p>
<p align="center">
  Descripción de la imagen
</p>
<p style="line/height: 1;">
Extraido de: https://msktc.org/sites/default/files/FactsFigures2021-Spanish-508.pdf
</p>

## 5. Diagrama de Ishikawa
<p style="line-height: 1.2;">
<strong>Figura 4</strong><br>
Falta de información sensorial en el cuerpo de un paciente con lesión medular.
</p>
<p align="center">
  Descripción de la imagen
</p>
<p style="line/height: 1;">
Extraido de: Elaboración propia
</p>

## 6. Definición de problematicas
Falta de información sensorial en el cuerpo de un paciente con lesión medular que puede realizar bipedestación y/o marcha.

## 7. Contexto científico
| **Título** | **Autor** | **Año de publicacíón** | **Resumen** | **Enlace** |
|-----------|--------------|-------------------------|------------|---------------|
| Uso de sensores inerciales en fisioterapia: Una aproximación a procesos de evaluación del movimiento humano | Julialba Castellanos Ruíz, Lina María Montealegre Mesa, Brahian Daniel Martíne Toro, Juan José Gallo Serna , Osvaldo Almanza Fuentes | <p align="center">2020</p> | Este artículo tiene como objetivo analizar  la  información  sobre  el  uso  de  sensores  inerciales como  una  aproximación  a  los  procesos  de  evaluación  del  movimiento  corporal  humano. Esta Unidad de Medición Inercial (IMU) es compatible con aplicaciones (APP), con el objetivo de obtener datos de movimiento tridimensionales y como evaluación e intervención, o que permita cuantificar los resultados de la acción motora. | <p align="center">[Más información](https://revistas.udenar.edu.co/index.php/usalud/article/view/5284/6932)</p> |
| Diseño de ayuda técnica para terapia física enfocada a personas con paraplejia: revisión de la literatura | Miranda Bañuelos, M., Meraz Tena, E. G., & Balderrama Armendáriz, C. O. | <p align="center">2019</p> | El artículo de la revista habla acerca de la utilidad del uso de la tecnología para ayudar en la rehabilitación de pacientes que tienen lesiones medulares | <p align="center">[Más información](https://doi.org/10.20983/culcyt.2019.1)</p> |
| Rehabilitación y readaptación de las lesiones medulares adquiridas del adulto: tetraplejias AIS A | C. Gournay; C.Hugeron | <p align="center">2024</p> | El artículo habla sobre el impacto de la tetraplejia AIS A (estadio A de la American Spinal Injury Association Impairment Scale) en la independencia y autonomía funcional de los pacientes. | <p align="center">[Más información](https://www.sciencedirect.com/science/article/pii/S1293296523486707)</p> |
| Sensores de movimiento portátiles para la rehabilitación: de la tecnología a la práctica clínica | Gerrit Ruben Hendrik Regterschot ,Gerard M. Ribbers, Juan B. J. Bussmann | <p align="center">2020</p> | Los trastornos motores aumentan debido al envejecimiento de la población, lo que demanda mejoras en la rehabilitación médica. Los sensores portátiles de movimiento pueden optimizar este proceso al proporcionar mediciones objetivas en diversos entornos. Aunque su potencial es grande, su uso en la práctica clínica sigue siendo limitado. Este número especial incluye 17 estudios que abordan el desarrollo de algoritmos, la validación de sensores y su aplicación en la rehabilitación motora. | <p align="center">[Más información](https://www.mdpi.com/1424-8220/21/14/4744)</p> |
| Plantar pressure measurement system based on piezoelectric sensor: a review | Xiang Li, Keyi Wang, Yan Lin Wang, Kui Cheng Wang | <p align="center">2022</p> | Este artículo revisa las tecnologías de medición de la fuerza plantar usando sensores piezoeléctricos, útiles para rehabilitación, diseño de calzado, diagnóstico clínico y deportes. Analiza los principios de funcionamiento y diseños de sensores, como monolaterales y multicapa. Aunque los sensores piezoeléctricos son sensibles y fáciles de fabricar, su eficacia varía con la disposición de los sensores, lo que subraya la necesidad de más investigación para mejorar los sistemas de medición. | <p align="center">[Más información](https://ieeexplore.ieee.org/abstract/document/9677765)</p> |

## 8. Bibliografía
- [1] : World Health Organization: WHO. (2024, 16 abril). Lesión de la médula espinal. https://www.who.int/es/news-room/fact-sheets/detail/spinal-cord-injury
- [2] : Lesión medular espinal | Hospital Nacional de Paraplejicos. (s. f.). https://hnparaplejicos.sanidad.castillalamancha.es/es/pacientes/lesion-medular
- [3] : National Spinal Cord Injury Statistical Center, Facts and Figures at a Glance. Birmingham, AL: University of Alabama at Birmingham, 2021 https://msktc.org/sites/default/files/FactsFigures2021-Spanish-508.pdf
- [4] : Resolución Directoral Nº 200-2021-SA-DG-INR , Instituto Nacional de Rehabilitación - Plataforma del Estado Peruano. https://www.gob.pe/institucion/inr/buscador?term=200-2021&institucion=inr&topic_id=&contenido=&sort_by=none
- [5] : Chávez-Cristóbal, O. (2022). Repercusión familiar y apoyo social en familias de pacientes con lesión medular. Revista Médica Herediana, 33(2), 102-112. https://doi.org/10.20453/rmh.v33i2.4243

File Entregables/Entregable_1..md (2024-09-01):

# Análisis del Caso

## 1. Definiciones de términos clave
- **Lesión de médula espinal (LME):** Trauma o daño de la médula espinal que tiene como resultado la pérdida de algunas funciones motoras y/o sensoriales; estas pueden ser totales o parciales.
- **Nivel sensitivo:** Ubicación específica en el cuerpo donde se produce la alteración de la sensación normal.
- **Autonomía vesical y gastrointestinal:** Capacidad del paciente en controlar las funciones de la vejiga e intestino que podría verse afectada por la lesión de médula espinal, dependiendo el nivel y gravedad de la lesión.
- **Trastornos neurovegetativos:** Son condiciones que afectan el sistema nervioso autónomo, que controla funciones involuntarias del cuerpo, tales como la frecuencia cardíaca, presión arterial, la digestión, la respiración y homeostasis
- **Tetraplejia:** también conocida como cuadriplejia, es la parálisis parcial o total de los miembros del cuerpo, brazos y piernas; está condición es causada por daño o lesión de la médula espinal, específicamente en la región cervical (cuello).

## 2. Desarrollo de la temática
Los daños producidos en la médula espinal por traumatismos (caídas y accidentes de tráfico) o por causas no traumáticas, como tumores, enfermedades degenerativas y vasculares, infecciones, toxinas o defectos congénitos son definidos como una lesión medular [1].  Este hecho se concreta en la pérdida del movimiento voluntario, de la sensibilidad, además se producen trastornos neurovegetativos, alteraciones de las funciones vesical e intestinal, del sistema cardiovascular, de la función sexual, entre otras complicaciones [2]. El grado de deterioro relacionado con una lesión medular depende de la gravedad de la lesión y de su localización en la médula espinal. La lesión medular provoca la pérdida completa o incompleta de las funciones sensoriales y/o motoras por debajo del nivel de la lesión [1].

Las lesiones de la médula espinal pueden afectar la capacidad para realizar actividades de la vida diaria, como caminar, utilizar los brazos, vaciar fisiológicamente el intestino o la vejiga, o lavarse y vestirse. Estas limitaciones se ven agravadas por, actitudes negativas y barreras físicas a la movilidad básica que limitan la independencia y la plena participación social, lo cual a corto plazo genera fuertes sentimientos de tristeza, culpa o inutilidad, este es motivo por el cual muchos llevan tratamientos psicológicos para poder afrontar su situación de la mejor manera.

## 3. Contexto nacional 
En nuestro país no hay estudios de incidencia, ni prevalencia de lesión medular, ni tampoco es posible estimar estos datos por no contar con data estandarizada ni con un sistema informático adecuado para realizar el reporte respectivo. Por lo cual se ha tornado en cuenta sólo fue reportado por el sistema informático del instituto Nacional de Rehabilitación “Dra. Adriana Rebaza Flores" AMISTAD PERÚ-JAPÓN, durante los años del 2012 al 2018 el Departamento de investigación, Docencia y Rehabilitación Integral en Lesiones Medulares ha atendido aproximadamente 1800 pacientes con lesión medular nuevos en consulta externa, y por año aproximadamente se ha atendido 260 pacientes nuevos (Io que equivale a 19% en promedio de las atenciones en este departamento), durante el periodo 2012 - 2018 el 45% de casos atendidos corresponden a causas traumáticas, el 43% a las no traumáticas, el 8% a las secuelas de poliomielitis. Asimismo, del 2014 al 2017 las causas de lesiones traumáticas se dividen en: 38% por accidentes de tránsito, 35% ocasionadas por caídas, y el 17% debido a lesiones de armas; porcentajes similares a los reportados por otros países (Estados Unidos) [4].

El sistema de diagnóstico y tratamiento que se realizan en nuestro país es clásico y tiene como objetivo disminuir la morbilidad y mortalidad derivada de las lesiones medulares, para esto se realizan un proceso de actividades como: Solicitar exámenes de laboratorio, estudios de imágenes; interconsultas; terapias físicas; instaurar medidas de prevención y dispositivos (camas especializadas, sillas, cojines); tratamiento farmacológico; orientación y consejos sobre sexualidad, fertilidad y gestación;  evaluaciones conductuales, psicológicas y psiquiátricas; etc.

Para clasificar a cada paciente, nuestros centros de rehabilitación siguen los Estándares Internacionales para la Clasificación Neurológica de la Lesión de la Médula Espinal (ISNCSCI), lo cual nos permite hacer un mejor enfoque en las zonas con repercusiones.

<p style="line-height: 1.2;">
<strong>Figura 1</strong><br>
Internacional Standards for Neurological Classification of SCI (ISNCSCI) Worksheet
</p>
<p align="center">
  Descripción de la imagen
</p>
<p style="line/height: 1;">
Extraido de: https://asia-spinalinjury.org/international-standards-neurological-classification-sci-isncsci-worksheet/
</p>

En el aspecto de hospitalización, nuestro protocolo se basa en evaluar el grado de lesión que tiene el paciente y asignarle un tratamiento adecuado que depende de cada caso presentado en el Instituto Nacional de Rehabilitación; algunas de las prácticas que se hacen en el área de hospitalización son: Aplicar técnicas atraumáticas de inserción de catéter; retirar SVP prontamente y reeducar las vías urinarias, si no hay contraindicaciones; cuidados de la piel y cambios posturales activos o pasivos; seguimiento de un plan nutricional especial para cada paciente y manejo conjunto para entrenamiento en movilizaciones y/o transferencias mediante técnicas seguras con apoyos técnicos y/o asistencia requerida según funcionalidad, asimismo, entrenamiento de técnicas de caídas y reincorporación a la silla de ruedas.

Según la Revista Médica Herediana, las revisiones sobre la repercusión de la lesión medular hacen referencia de lo complejo que resulta para una persona portadora de una lesión medular y su familia convivir con esta condición. Los aspectos psicosociales, especialmente el apoyo social, son tan importantes como los aspectos clínicos cuando se habla de la calidad de vida en las personas que presentan una lesión medular espinal (LME). Sin embargo, cabe mencionar que se han encontrado pocos estudios sobre la repercusión familiar y apoyo social en las familias de personas con lesión medular, la mayoría de estudios estuvieron relacionados a la discapacidad como tema general. La población de estudio observada a continuación estuvo conformada por todos los familiares de pacientes con LME que se encontraron hospitalizados y recibieron tratamiento de rehabilitación desde Septiembre a diciembre del 2019 [5].

<p style="line-height: 1.2;">
<strong>Tabla 1</strong><br>
Características generales del paciente con lesión medular 
</p>
<p align="center">
  Descripción de la imagen
</p>
<p style="line/height: 1;">
Extraido de: https://doi.org/10.20453/rmh.v33i2.4243
</p>

<p style="line-height: 1.2;">
<strong>Tabla 2</strong><br>
Repercusión familiar por áreas y global en pacientes con lesión medular 
</p>
<p align="center">
  Descripción de la imagen
</p>
<p style="line/height: 1;">
Extraido de: https://doi.org/10.20453/rmh.v33i2.4243
</p>

Se encontró que los pacientes de 18 a más años tienen menos prevalencia de repercusión familiar severa que los pacientes que tienen de 12 a 17 años, lo que podría explicarse porque en los adolescentes se acentúan los cambios que presentan en su cuerpo y corporalidad en el cambio de la imagen de sí mismo, las relaciones contradictorias   principalmente   con   su   familia   y   amigos, la carga de la discapacidad y el proceso de adaptación a su condición. También, el 44% de los pacientes y el 58% de los familiares tenían entre 30 y 59 años. El 34% de los cuidadores eran cónyuges del paciente, el 48% era familia de tipo nuclear y el 62% de las familias pertenecieron al nivel socioeconómico de pobreza extrema. El 78% de los pacientes tenían paraplejía y el 48% lesión tipo ASIA A. La repercusión global, fue elevada en 68% y con un sentido negativo en 94% de los casos [5].   

Los resultados de esta investigación se deben interpretar con cautela, primero, no se tuvo el poder estadístico suficiente para encontrar la asociación entre el apoyo social y la repercusión familiar ya que no se calculó tamaño de muestra porque no se encontraron datos de otras investigaciones que sean de utilidad para dicho cálculo, por lo que, solo se evaluaron a todos los familiares de los pacientes con lesión medular que cumplan los criterios de selección en un periodo de tres meses. Segundo, el apoyo social y repercusión familiar podría variar dependiendo del nivel de atención, categorización y ubicación de la institución prestadora de servicios de salud en los que los pacientes y familiares se atienden; incluso si éstos no están institucionalizados [5].

## 4. Contexto mundial 
A nivel mundial, las lesiones medulares (SCI)  son una de las principales causas de discapacidad de larga duración, las estimaciones indican que aproximadamente 15,4 millones de personas tenían una lesión en la médula espinal en 2021 [1] .Las estadísticas que muestra el Centro Nacional de Estadística sobre Lesiones de la Médula Espinal (NSCISC) indican lo siguiente:
Los accidentes automovilísticos son la principal causa de lesiones más reciente, seguidos de cerca por las caídas. Los actos de violencia (en primer lugar, las heridas de bala) y las actividades deportivas/recreativas también son causas relativamente frecuentes  [3].

<p style="line-height: 1.2;">
<strong>Figura 2</strong><br>
Estadisticas de las causas de lesiones medulares 
</p>
<p align="center">
  Descripción de la imagen
</p>
<p style="line/height: 1;">
Extraido de: https://msktc.org/sites/default/files/FactsFigures2021-Spanish-508.pdf
</p>

A nivel neurológico y magnitud de lesión la tetraplejia incompleta es la categoría neurológica más frecuente. La frecuencia de la paraplejia incompleta y la completa es prácticamente la misma. Menos del 1 % de las personas tuvieron una recuperación neurológica completa para cuando recibieron el alta médica  [3].

<p style="line-height: 1.2;">
<strong>Figura 3</strong><br>
Estadisticas de la magnitud de la lesión en lesiones medulares 
</p>
<p align="center">
  Descripción de la imagen
</p>
<p style="line/height: 1;">
Extraido de: https://msktc.org/sites/default/files/FactsFigures2021-Spanish-508.pdf
</p>

También, observamos que el promedio de esperanza de vida de las personas con SCI no ha mejorado desde la década de 1980 al 2015 y sigue estando muy por debajo de la esperanza de vida de las personas sin SCI. Los índices de mortalidad son considerablemente más altos durante el primer año después de la lesión que en los años siguientes, sobre todo en el caso de las personas con un deterioro neurológico más grave [3].

<p style="line-height: 1.2;">
<strong>Tabla 3</strong><br>
Esperanza de vida (años) después de la lesión según la gravedad de la lesión y la edad al lesionarse 
</p>
<p align="center">
  Descripción de la imagen
</p>
<p style="line/height: 1;">
Extraido de: https://msktc.org/sites/default/files/FactsFigures2021-Spanish-508.pdf
</p>

## 5. Diagrama de Ishikawa
<p style="line-height: 1.2;">
<strong>Figura 4</strong><br>
Falta de independencia en actividades cotidianas que afectan al paciente en funciones físicas, biológicas y psicológicas
</p>
<p align="center">
  Descripción de la imagen
</p>
<p style="line/height: 1;">
Extraido de: Elaboración propia
</p>

## 6. Definición de problematicas
La falta de independencia en actividades cotidianas afecta al paciente  en funciones físicas, biológicas y psicológicas

## 7. Contexto científico
| **Título** | **Autor** | **Año de publicacíón** | **Resumen** | **Enlace** |
|-----------|--------------|-------------------------|------------|---------------|
| Diseño de un exoesqueleto robótico de extremidades inferiores para el control del equilibrio de parapléjicos | MTC Perera, APA Madupriya, BDS Kaushalya, RKPS Ranaweera y RARC Gopura | <p align="center">2021</p> | En este artículo se propone un exoesqueleto robótico para extremidades inferiores que permite mantener el equilibrio de un paciente parapléjico durante la marcha | <p align="center">[Más información](https://ieeexplore.ieee.org/document/9463507)</p> |
| Diseño de ayuda técnica para terapia física enfocada a personas con paraplejia: revisión de la literatura | Miranda Bañuelos, M., Meraz Tena, E. G., & Balderrama Armendáriz, C. O. | <p align="center">2019</p> | El artículo de la revista habla acerca de la utilidad del uso de la tecnología para ayudar en la rehabilitación de pacientes que tienen lesiones medulares | <p align="center">[Más información](https://doi.org/10.20983/culcyt.2019.1)</p> |
| Nuevas tecnologías en neurorrehabilitación aplicadas al tratamiento del paciente con lesión medular | A.M Gil Agudo | <p align="center">2019</p> | El artículo propone el uso de un exoesqueleto portable para mayor independencia en la movilidad del paciente utilizando la señal eléctrica del cerebro a través de electrodos implantados para manejar los dispositivos | <p align="center">[Más información](https://www.sciencedirect.com/science/article/abs/pii/S0304541219300757)</p> |
| BMI Basada en imaginación motora de la marcha para el control de un exoesqueleto en pacientes con lesión medular | Ferrero, Laura; Quiles, Vicente; Ortiz, Mario; Iáñez, Eduardo; Azorín, José M. | <p align="center">2022</p> | Este artículo se centra en las interfaces cerebro-máquina (BMI de brain-machine interfaces) basadas en la imaginación motora se pueden utilizar para el control de dispositivos robóticos de asistencia y ofrecen una estrategia efectiva para la recuperación motora | <p align="center">[Más información](https://ruc.udc.es/dspace/handle/2183/31357)</p> |
| Enhanced Robot Arm at the Edge with NLP and Vision Systems | Pascal Sikorski, Kaleb Yu, Lucy Billadeau, Flavio Esposito, Hadi AliAkbarpour and Madi Babaiasl | <p align="center">2024</p> | Brazo robótico que puede interpretar y ejecutar comandos complejos a través de instrucciones de lenguaje natural usando LLMs/ GPT. Eficaz para usuarios con discapacidad (como lesión medular) que necesiten asistencia natural para su vida diaria. | <p align="center">[Más información](https://arxiv.org/abs/2405.17665)</p> |

## 8. Bibliografía
- [1] : World Health Organization: WHO. (2024, 16 abril). Lesión de la médula espinal. https://www.who.int/es/news-room/fact-sheets/detail/spinal-cord-injury
- [2] : Lesión medular espinal | Hospital Nacional de Paraplejicos. (s. f.). https://hnparaplejicos.sanidad.castillalamancha.es/es/pacientes/lesion-medular
- [3] : National Spinal Cord Injury Statistical Center, Facts and Figures at a Glance. Birmingham, AL: University of Alabama at Birmingham, 2021 https://msktc.org/sites/default/files/FactsFigures2021-Spanish-508.pdf
- [4] : Resolución Directoral Nº 200-2021-SA-DG-INR , Instituto Nacional de Rehabilitación - Plataforma del Estado Peruano. https://www.gob.pe/institucion/inr/buscador?term=200-2021&institucion=inr&topic_id=&contenido=&sort_by=none
- [5] : Chávez-Cristóbal, O. (2022). Repercusión familiar y apoyo social en familias de pacientes con lesión medular. Revista Médica Herediana, 33(2), 102-112. https://doi.org/10.20453/rmh.v33i2.4243

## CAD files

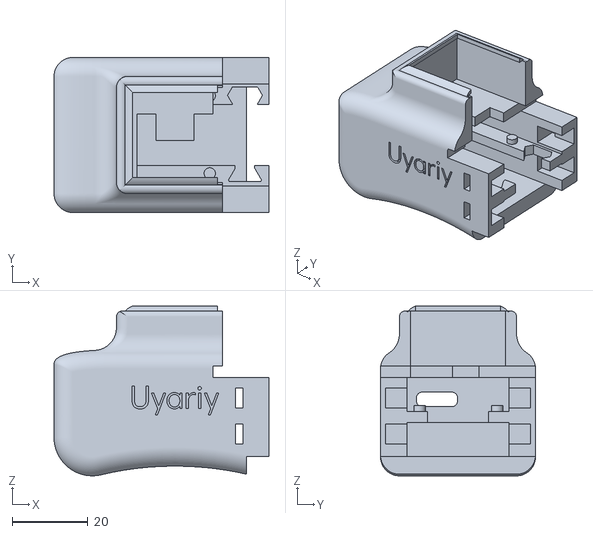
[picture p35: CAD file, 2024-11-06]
Hardware/Primer Prototipo del Modelo/Dispositivo de Medicion/Pieza de medicion 1/Pieza de medicion 1.stl
56.9 x 41.0 x 44.9

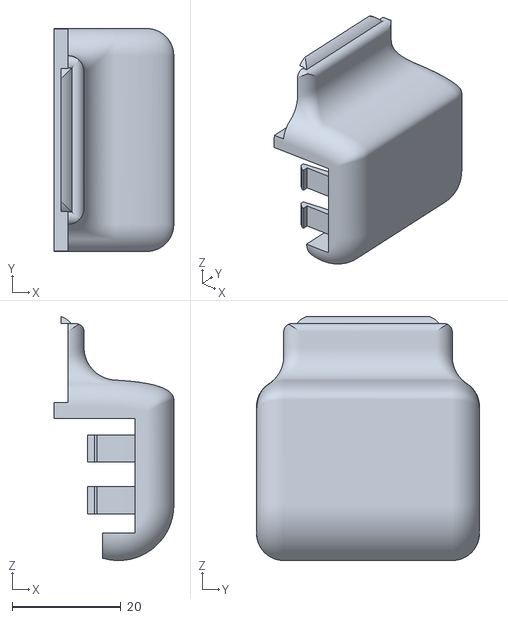
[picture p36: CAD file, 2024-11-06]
Hardware/Primer Prototipo del Modelo/Dispositivo de Medicion/Pieza de medicion 2/Pieza de medicion 2.stl
22.0 x 41.0 x 44.9

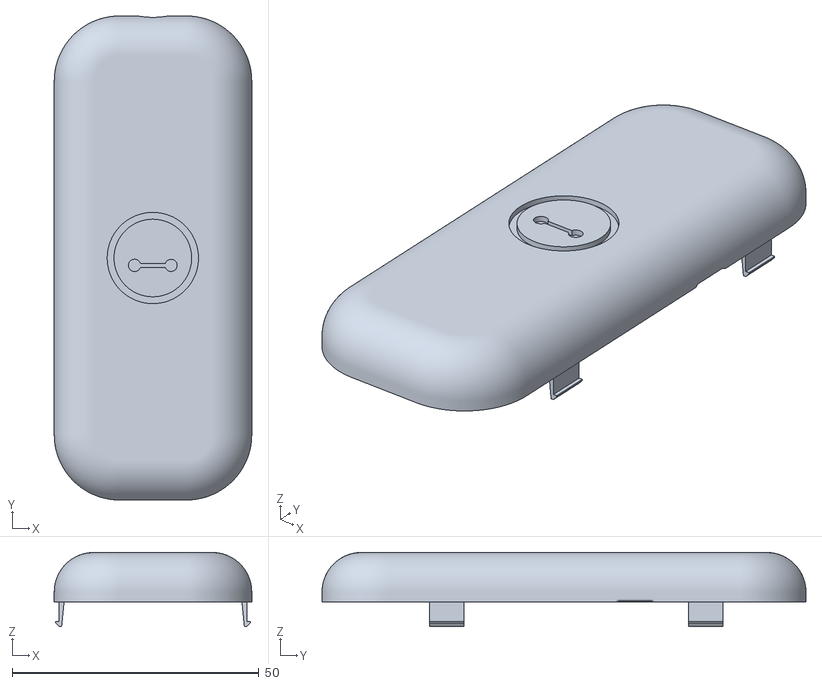
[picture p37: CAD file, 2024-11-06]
Hardware/Primer Prototipo del Modelo/Dispositivo Sensorial/Pieza sensorial 1/Pieza sensorial 1.stl
40.0 x 98.0 x 15.0

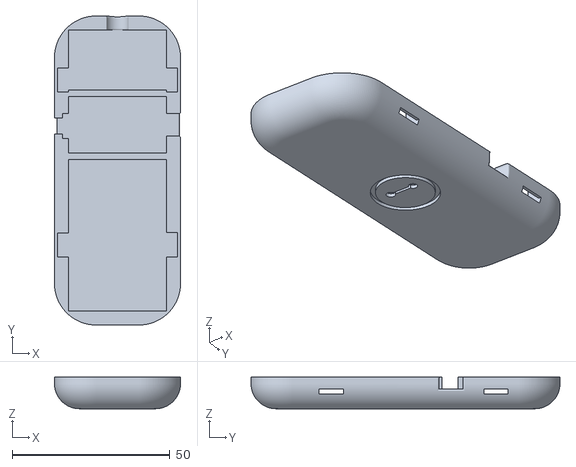
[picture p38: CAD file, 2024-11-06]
Hardware/Primer Prototipo del Modelo/Dispositivo Sensorial/Pieza sensorial 2/Pieza sensorial 2.stl
40.0 x 98.0 x 10.0

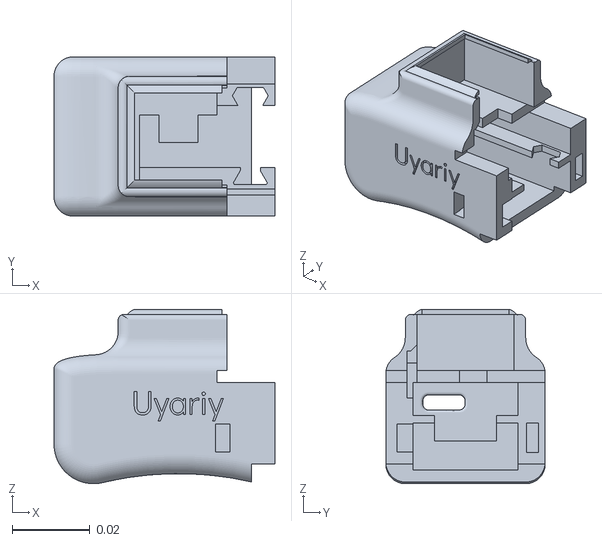
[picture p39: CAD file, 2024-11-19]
Hardware/Segundo Prototipo del Modelo/Dispositivo de Medicion/Pieza de medicion 1/Pieza de medicion 1.stl
0.0569 x 0.041 x 0.0449

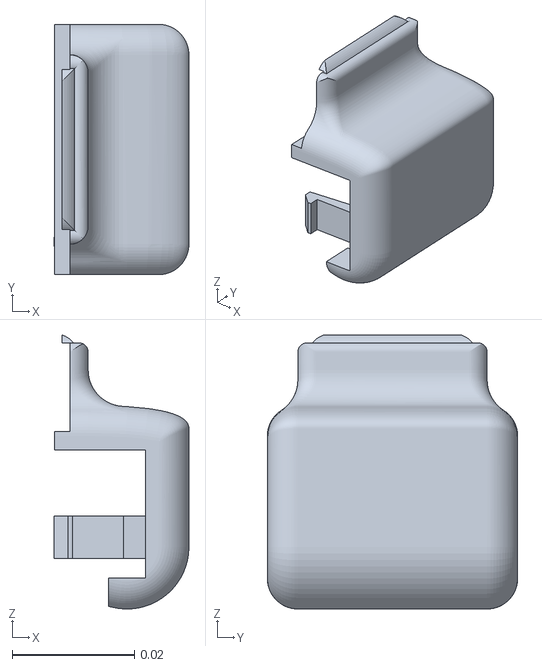
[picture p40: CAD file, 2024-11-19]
Hardware/Segundo Prototipo del Modelo/Dispositivo de Medicion/Pieza de medicion 2/Pieza de medicion 2.stl
0.0221 x 0.041 x 0.0449

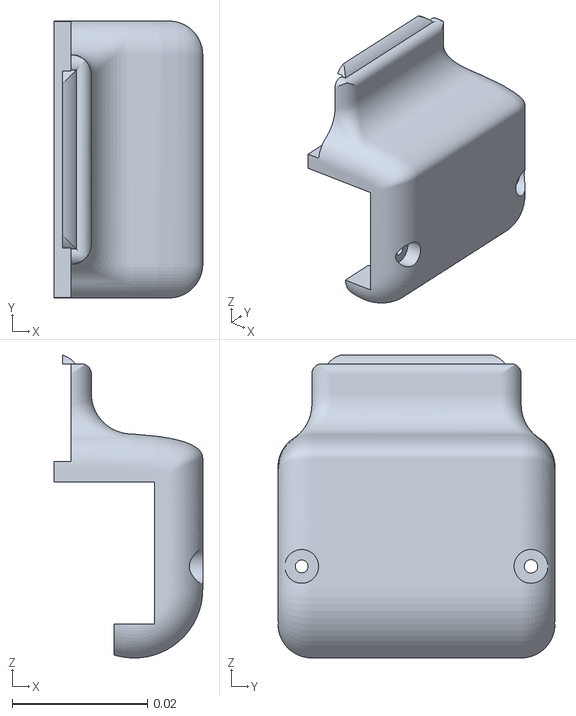
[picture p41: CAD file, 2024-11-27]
Hardware/Tercer Prototipo del Modelo/Dispositivo de Medicion/Parte de la tapa/Parte de la tapa.stl
0.022 x 0.041 x 0.0449

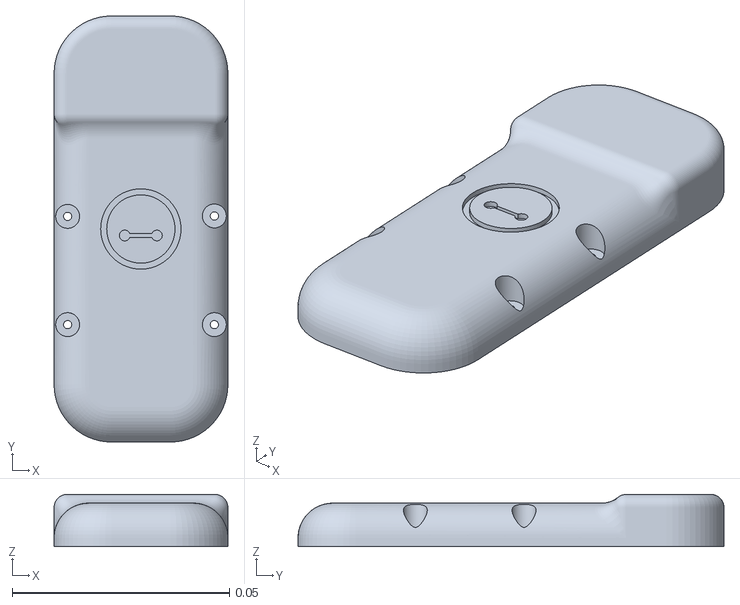
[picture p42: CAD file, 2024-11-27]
Hardware/Tercer Prototipo del Modelo/Dispositivo Sensorial/Parte de la base/Parte de la base.stl
0.04 x 0.098 x 0.012

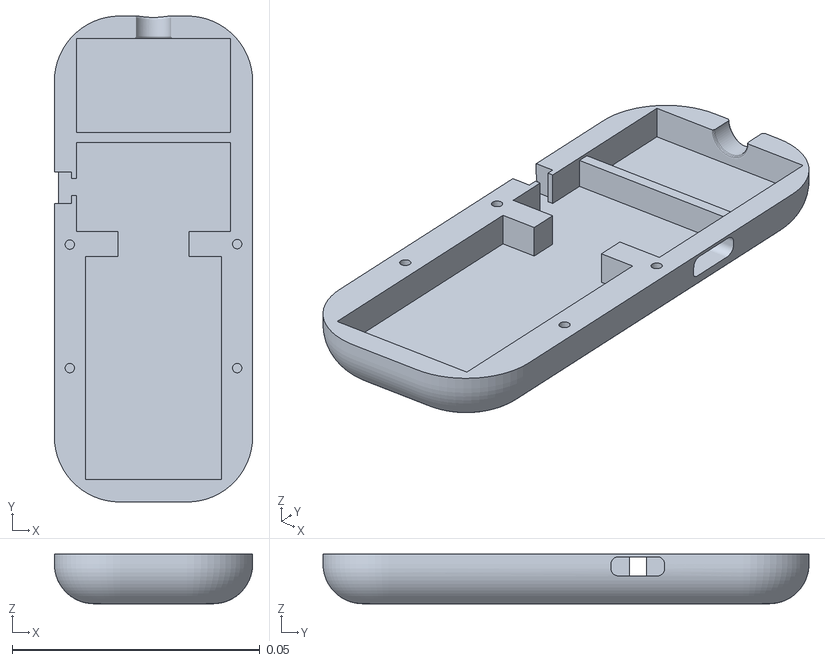
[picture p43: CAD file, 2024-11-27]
Hardware/Tercer Prototipo del Modelo/Dispositivo Sensorial/Parte de la tapa/Parte de la tapa.stl
0.04 x 0.098 x 0.01

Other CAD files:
Hardware/Tercer Prototipo del Modelo/Dispositivo de Medicion/Parte del cuerpo/Parte del cuerpo.stl

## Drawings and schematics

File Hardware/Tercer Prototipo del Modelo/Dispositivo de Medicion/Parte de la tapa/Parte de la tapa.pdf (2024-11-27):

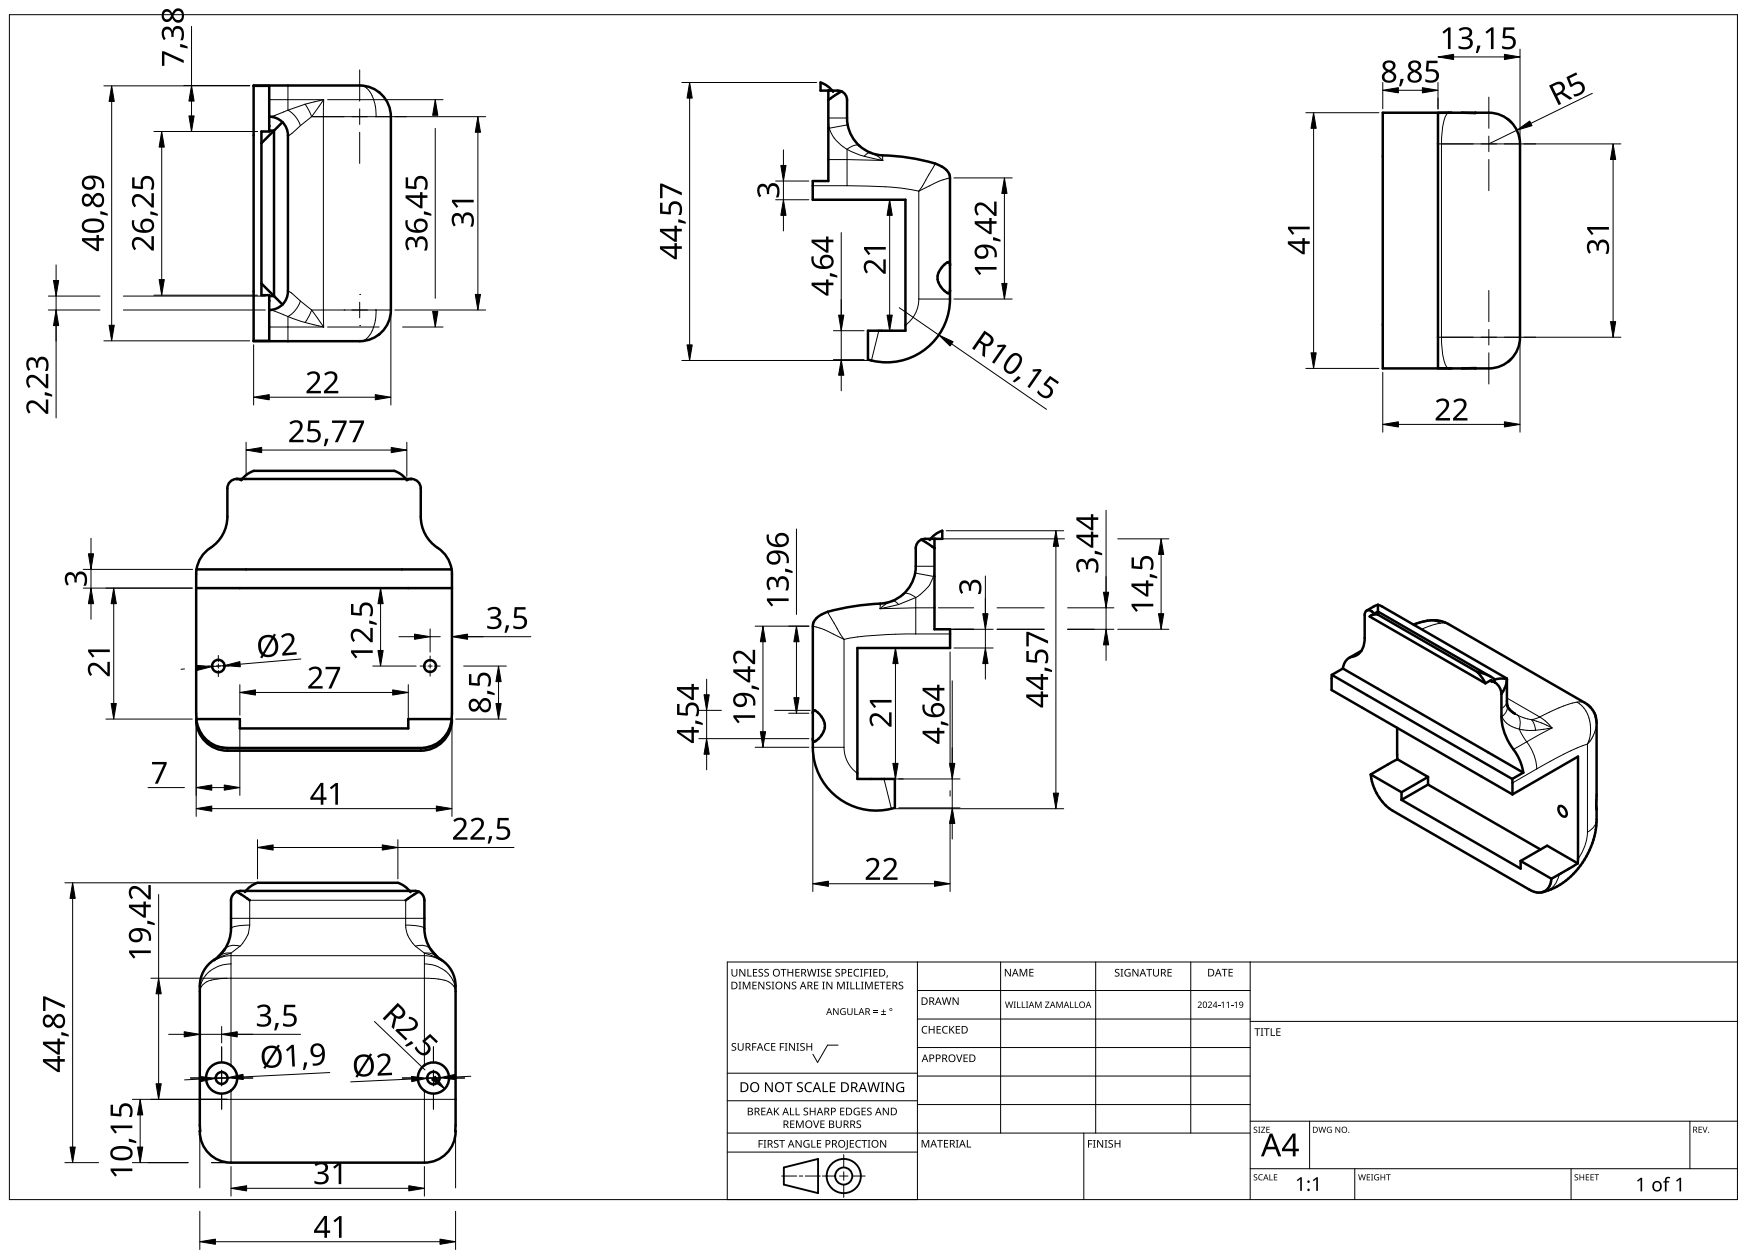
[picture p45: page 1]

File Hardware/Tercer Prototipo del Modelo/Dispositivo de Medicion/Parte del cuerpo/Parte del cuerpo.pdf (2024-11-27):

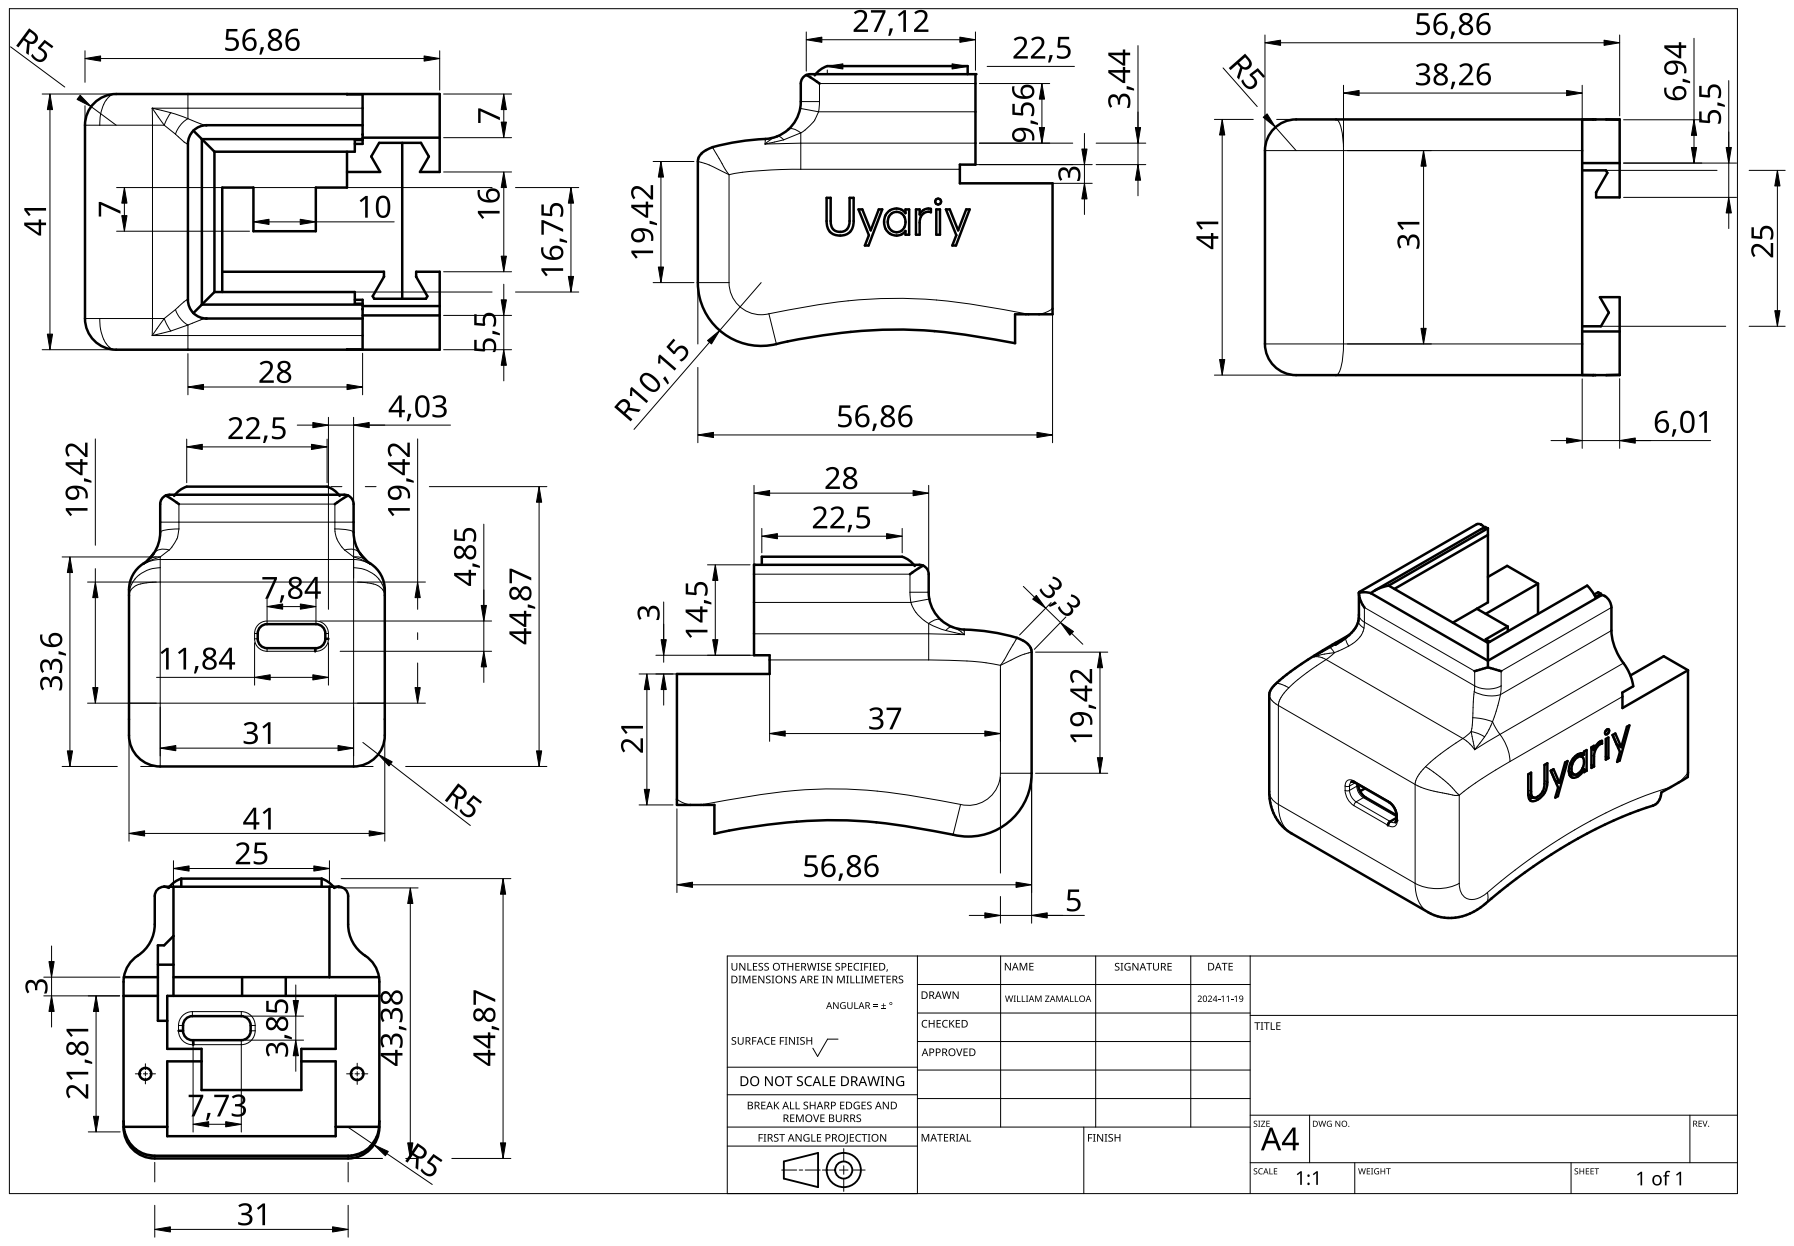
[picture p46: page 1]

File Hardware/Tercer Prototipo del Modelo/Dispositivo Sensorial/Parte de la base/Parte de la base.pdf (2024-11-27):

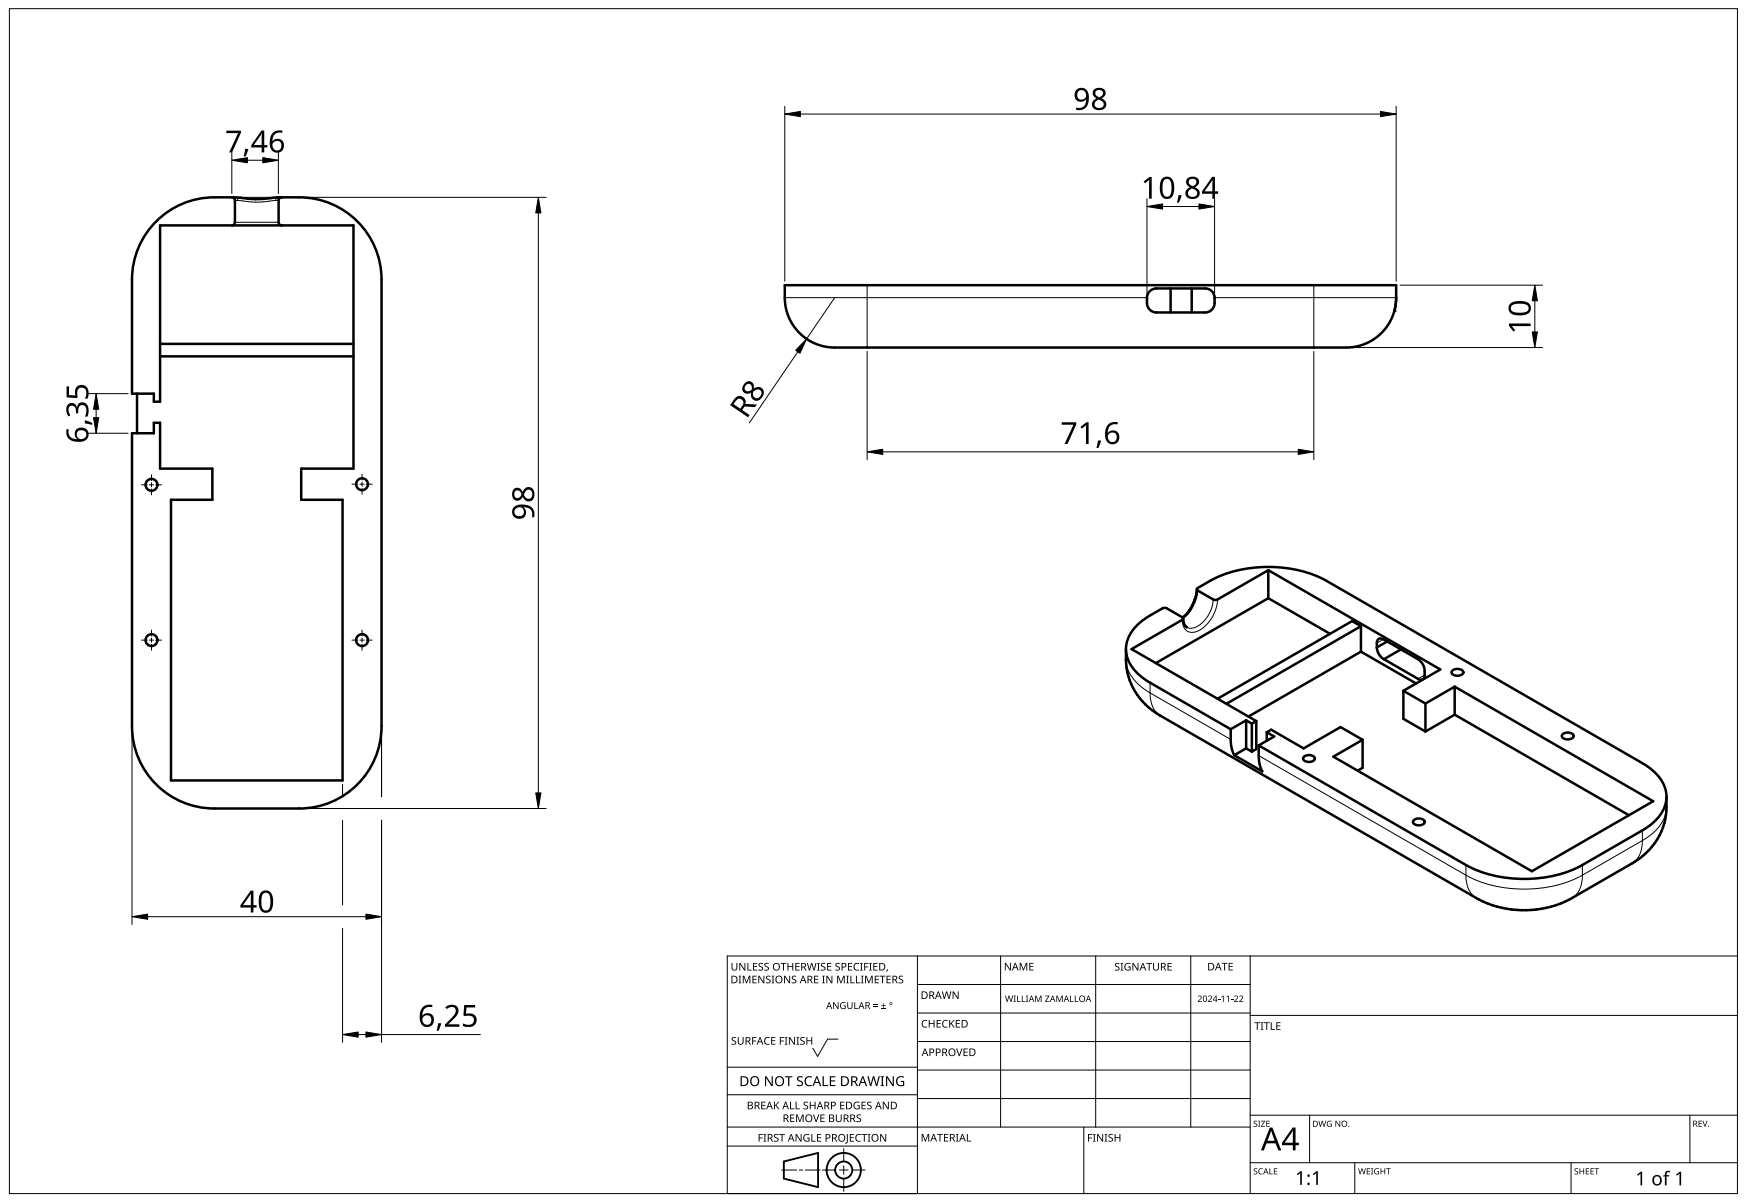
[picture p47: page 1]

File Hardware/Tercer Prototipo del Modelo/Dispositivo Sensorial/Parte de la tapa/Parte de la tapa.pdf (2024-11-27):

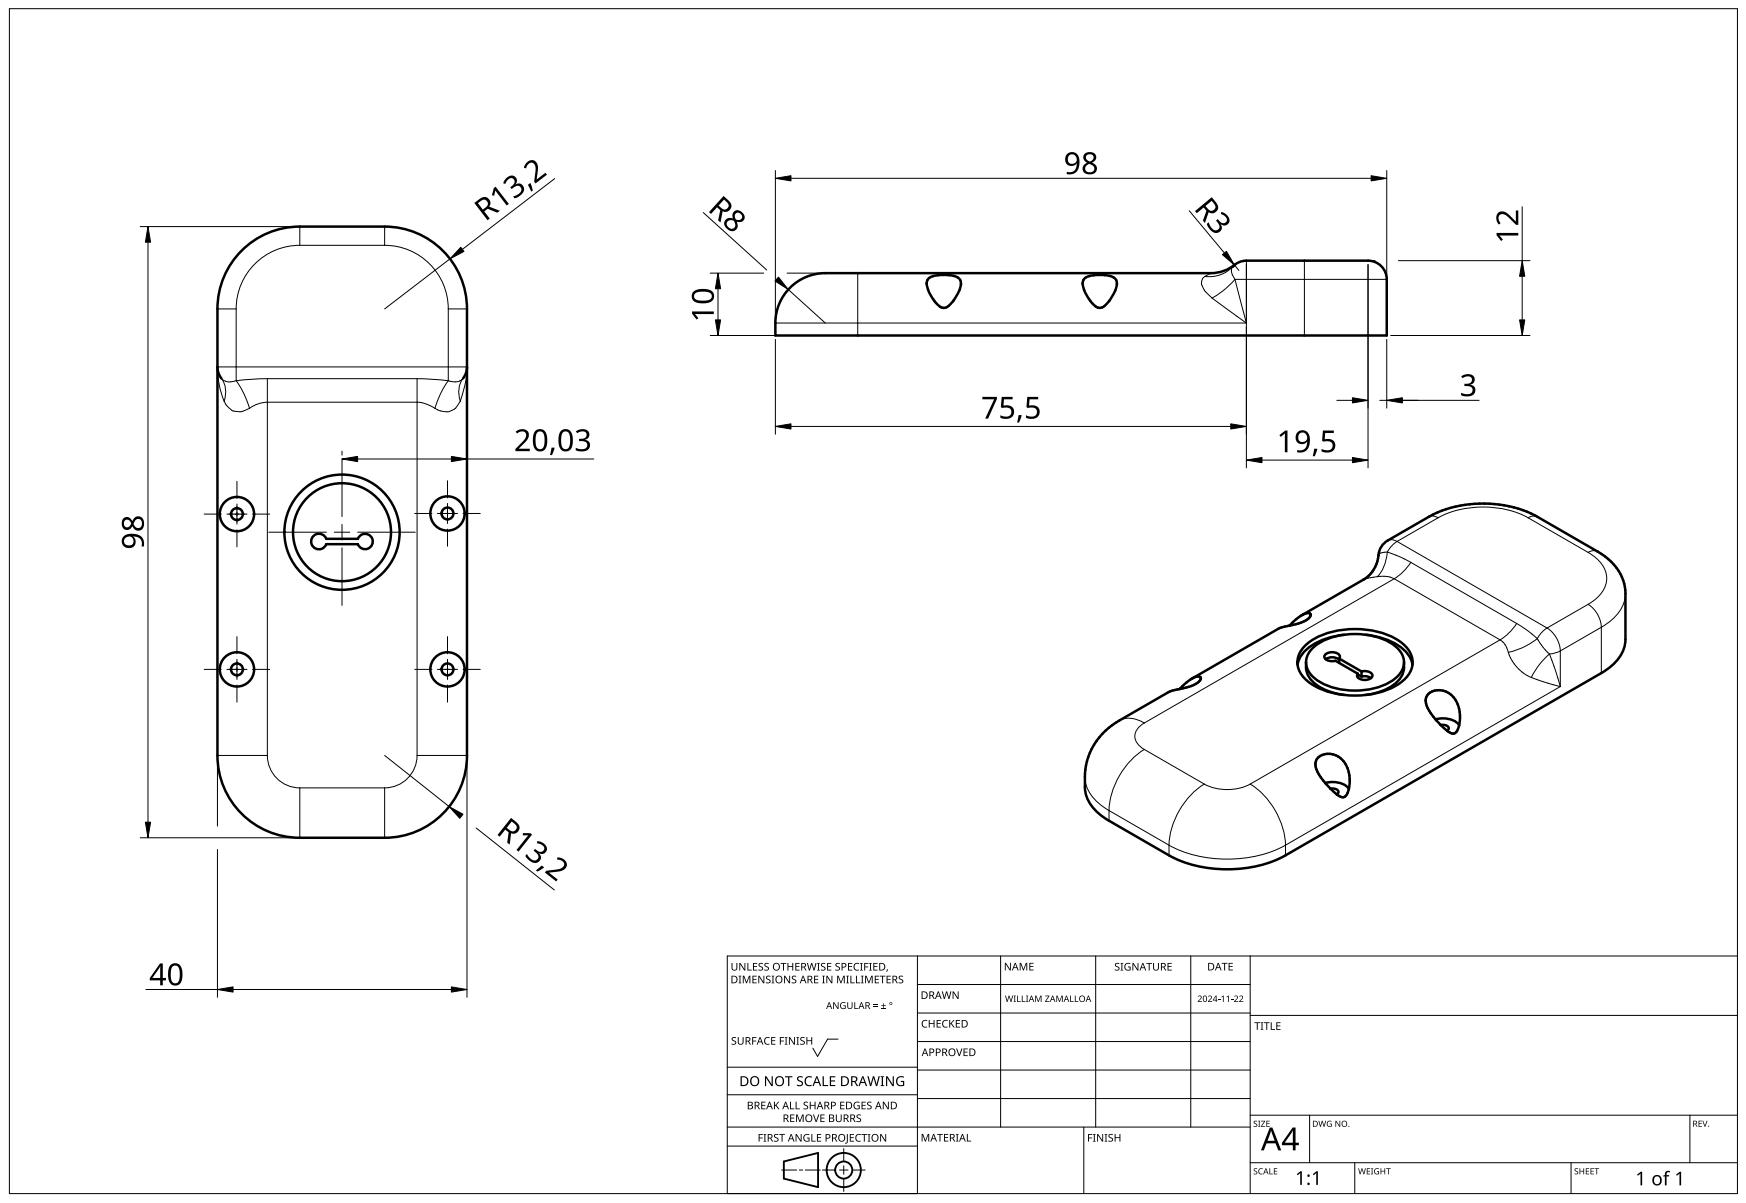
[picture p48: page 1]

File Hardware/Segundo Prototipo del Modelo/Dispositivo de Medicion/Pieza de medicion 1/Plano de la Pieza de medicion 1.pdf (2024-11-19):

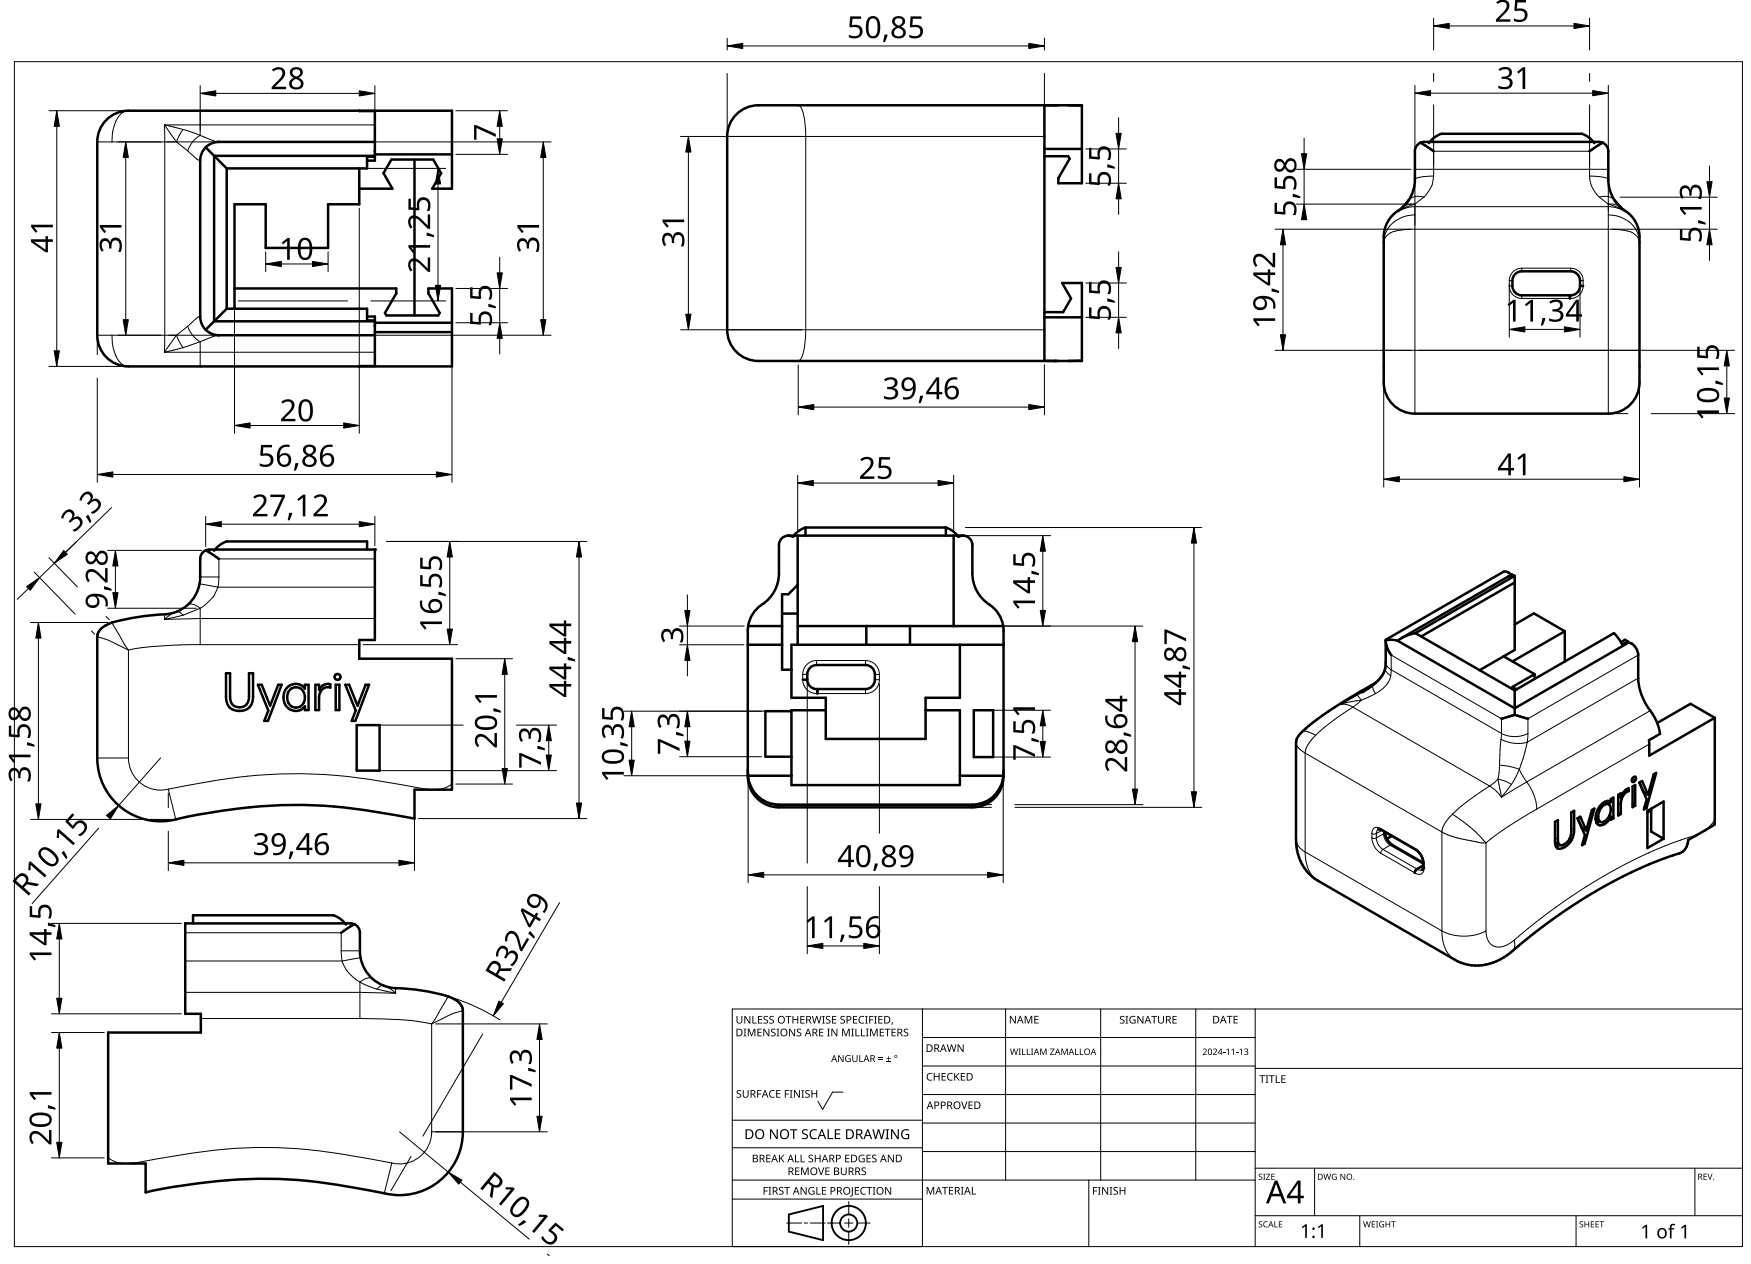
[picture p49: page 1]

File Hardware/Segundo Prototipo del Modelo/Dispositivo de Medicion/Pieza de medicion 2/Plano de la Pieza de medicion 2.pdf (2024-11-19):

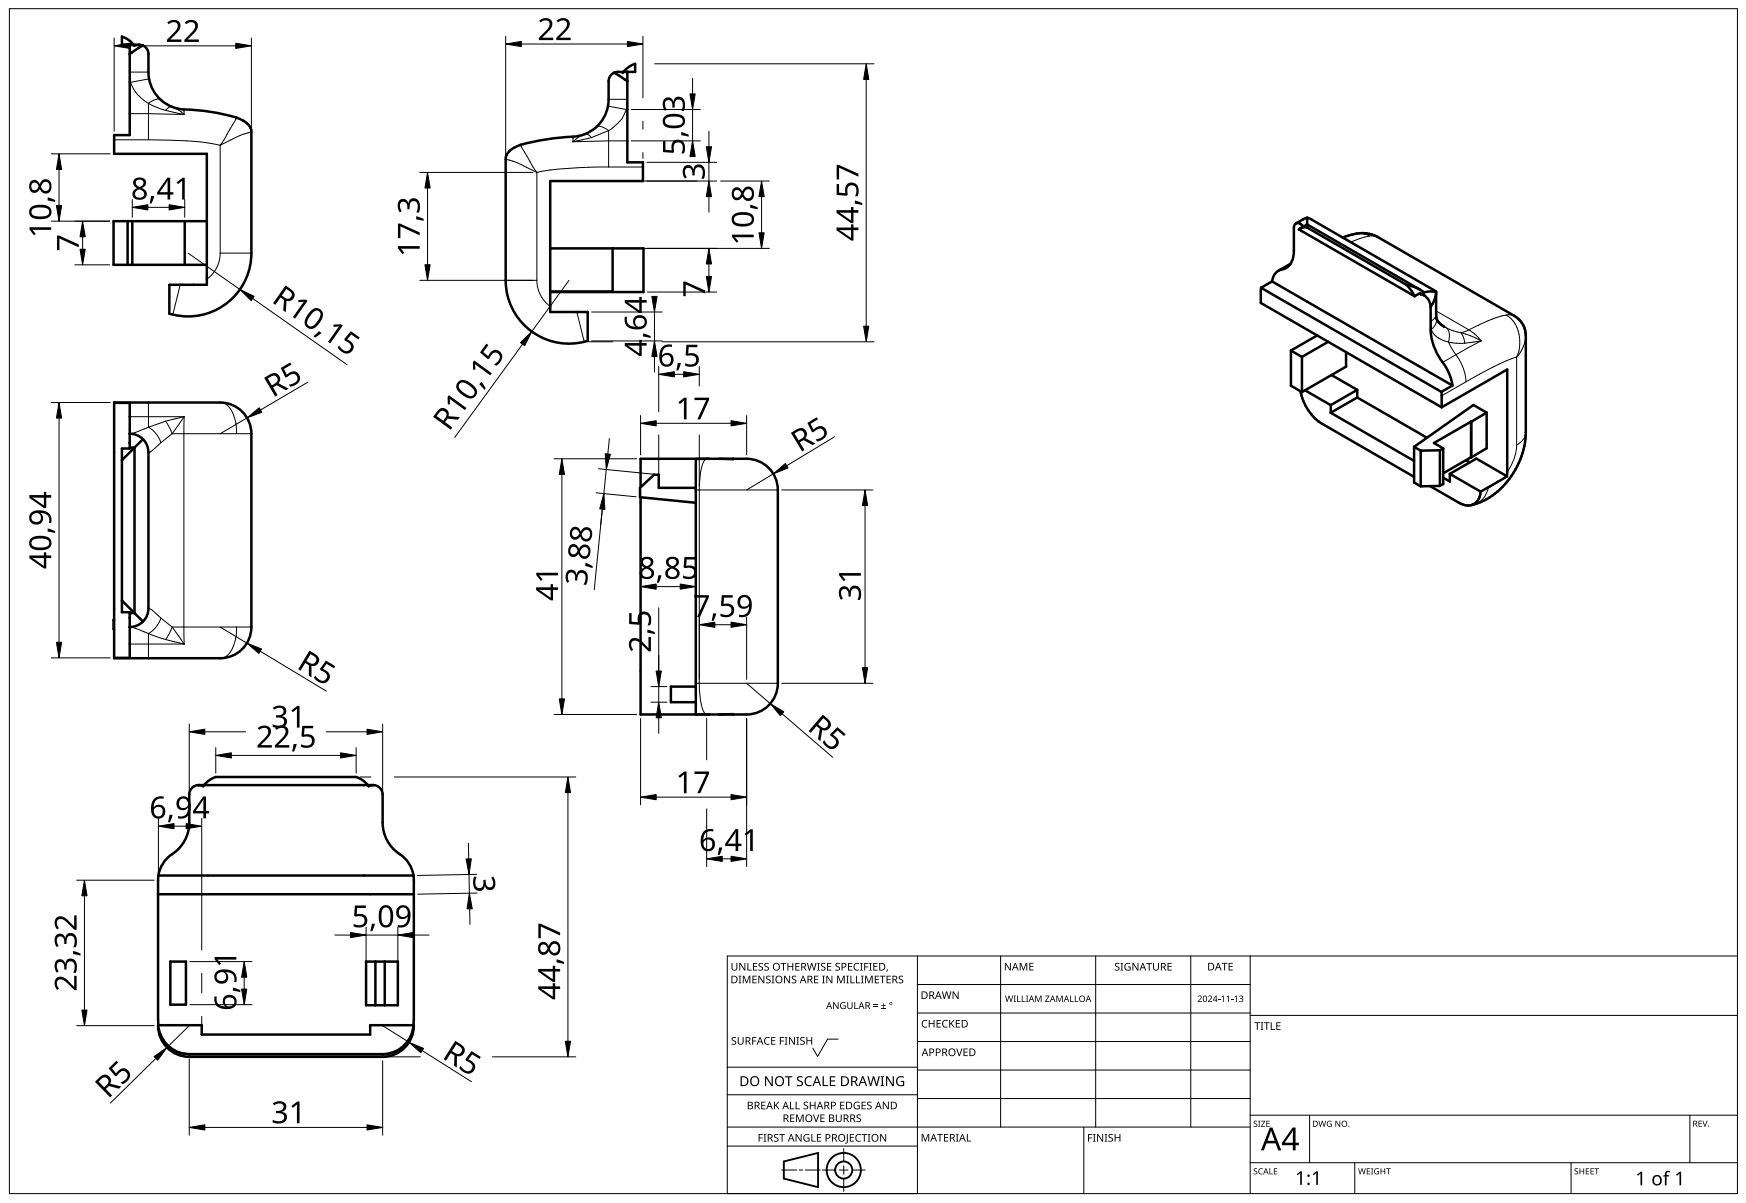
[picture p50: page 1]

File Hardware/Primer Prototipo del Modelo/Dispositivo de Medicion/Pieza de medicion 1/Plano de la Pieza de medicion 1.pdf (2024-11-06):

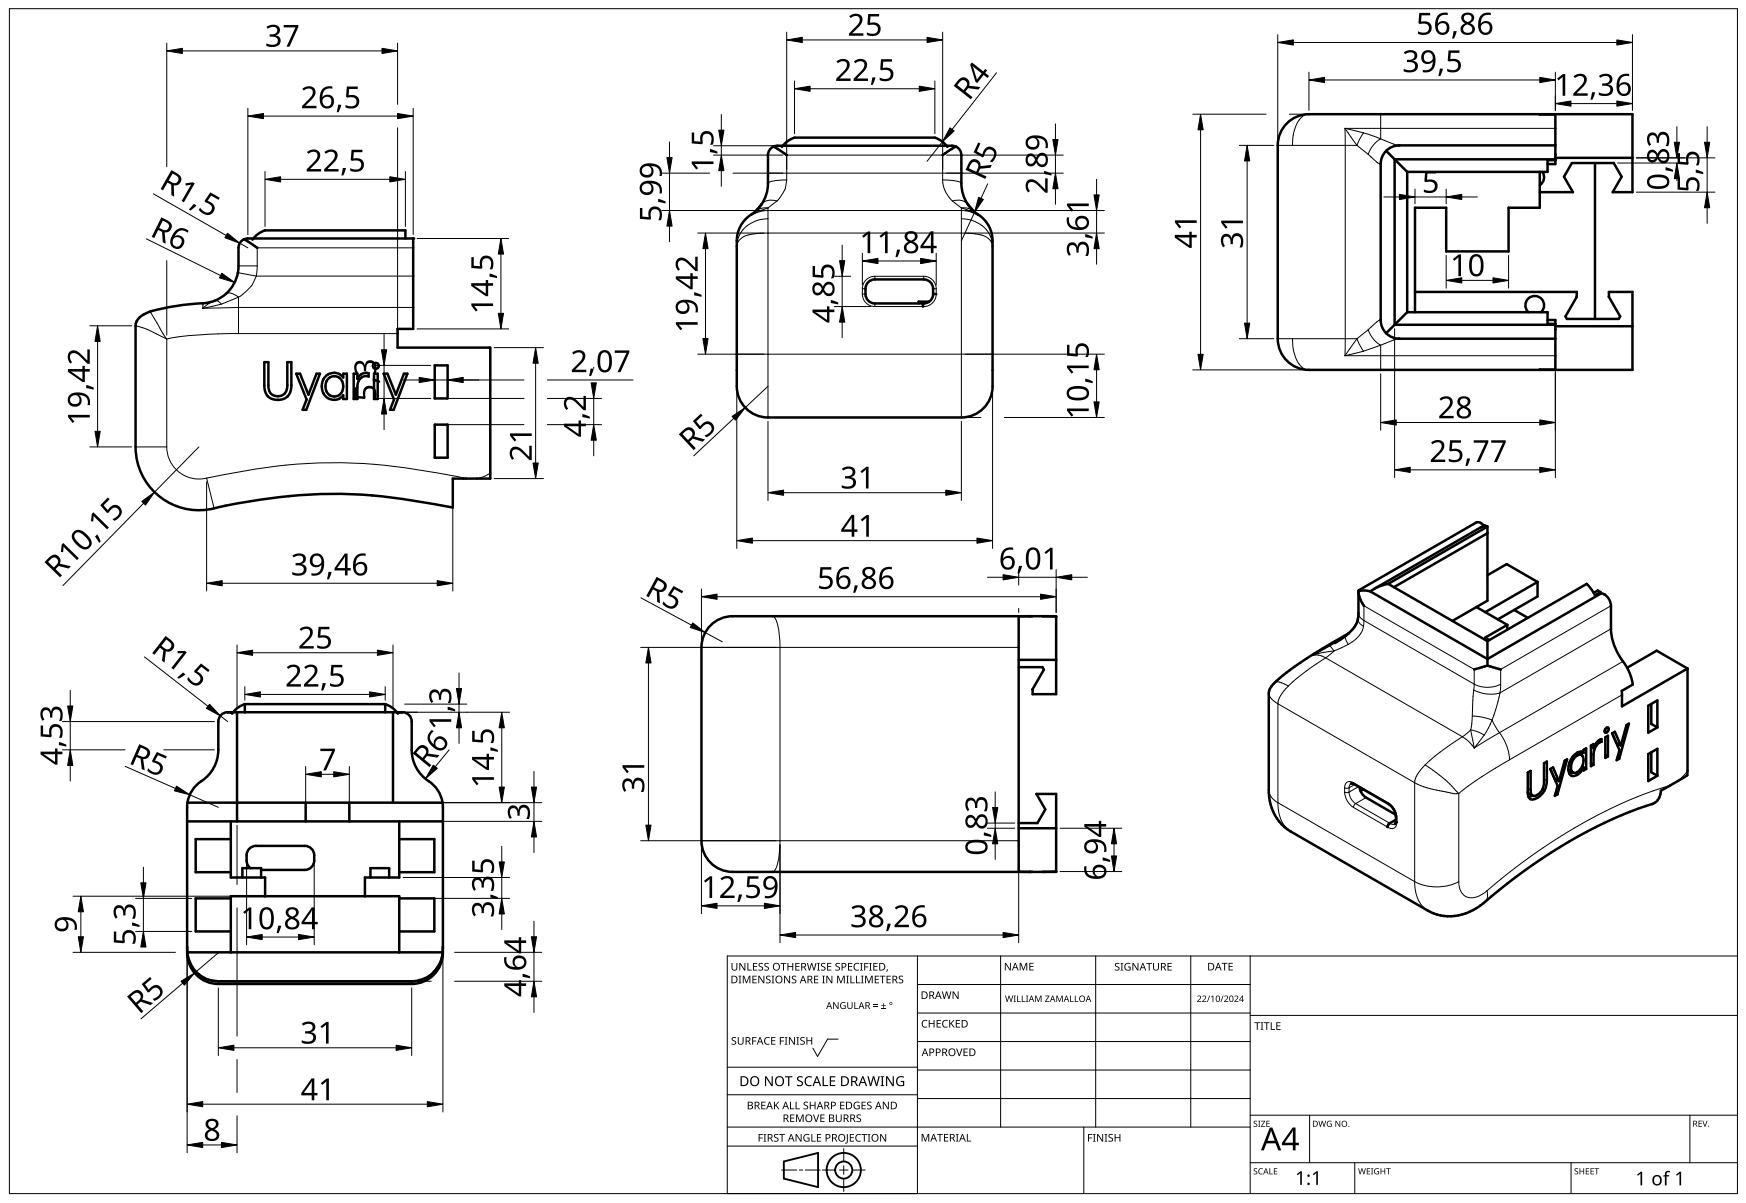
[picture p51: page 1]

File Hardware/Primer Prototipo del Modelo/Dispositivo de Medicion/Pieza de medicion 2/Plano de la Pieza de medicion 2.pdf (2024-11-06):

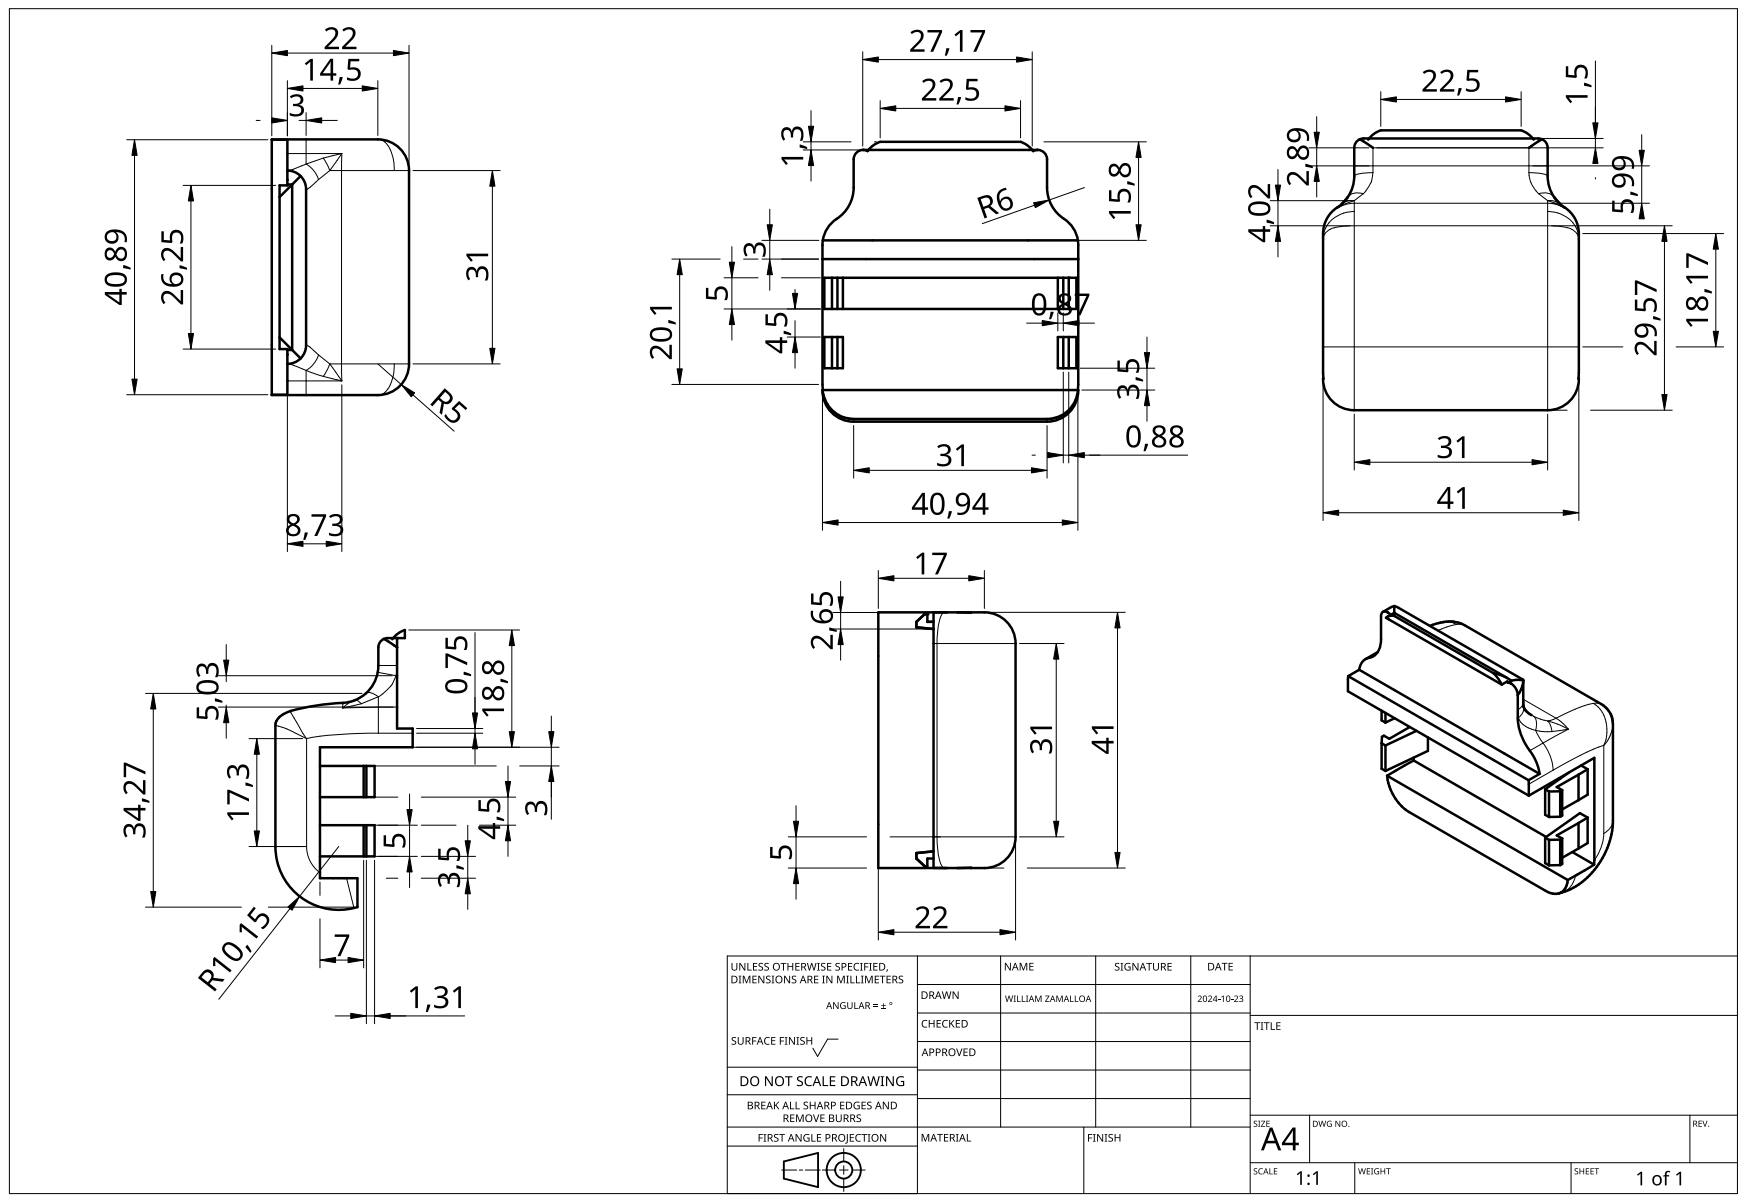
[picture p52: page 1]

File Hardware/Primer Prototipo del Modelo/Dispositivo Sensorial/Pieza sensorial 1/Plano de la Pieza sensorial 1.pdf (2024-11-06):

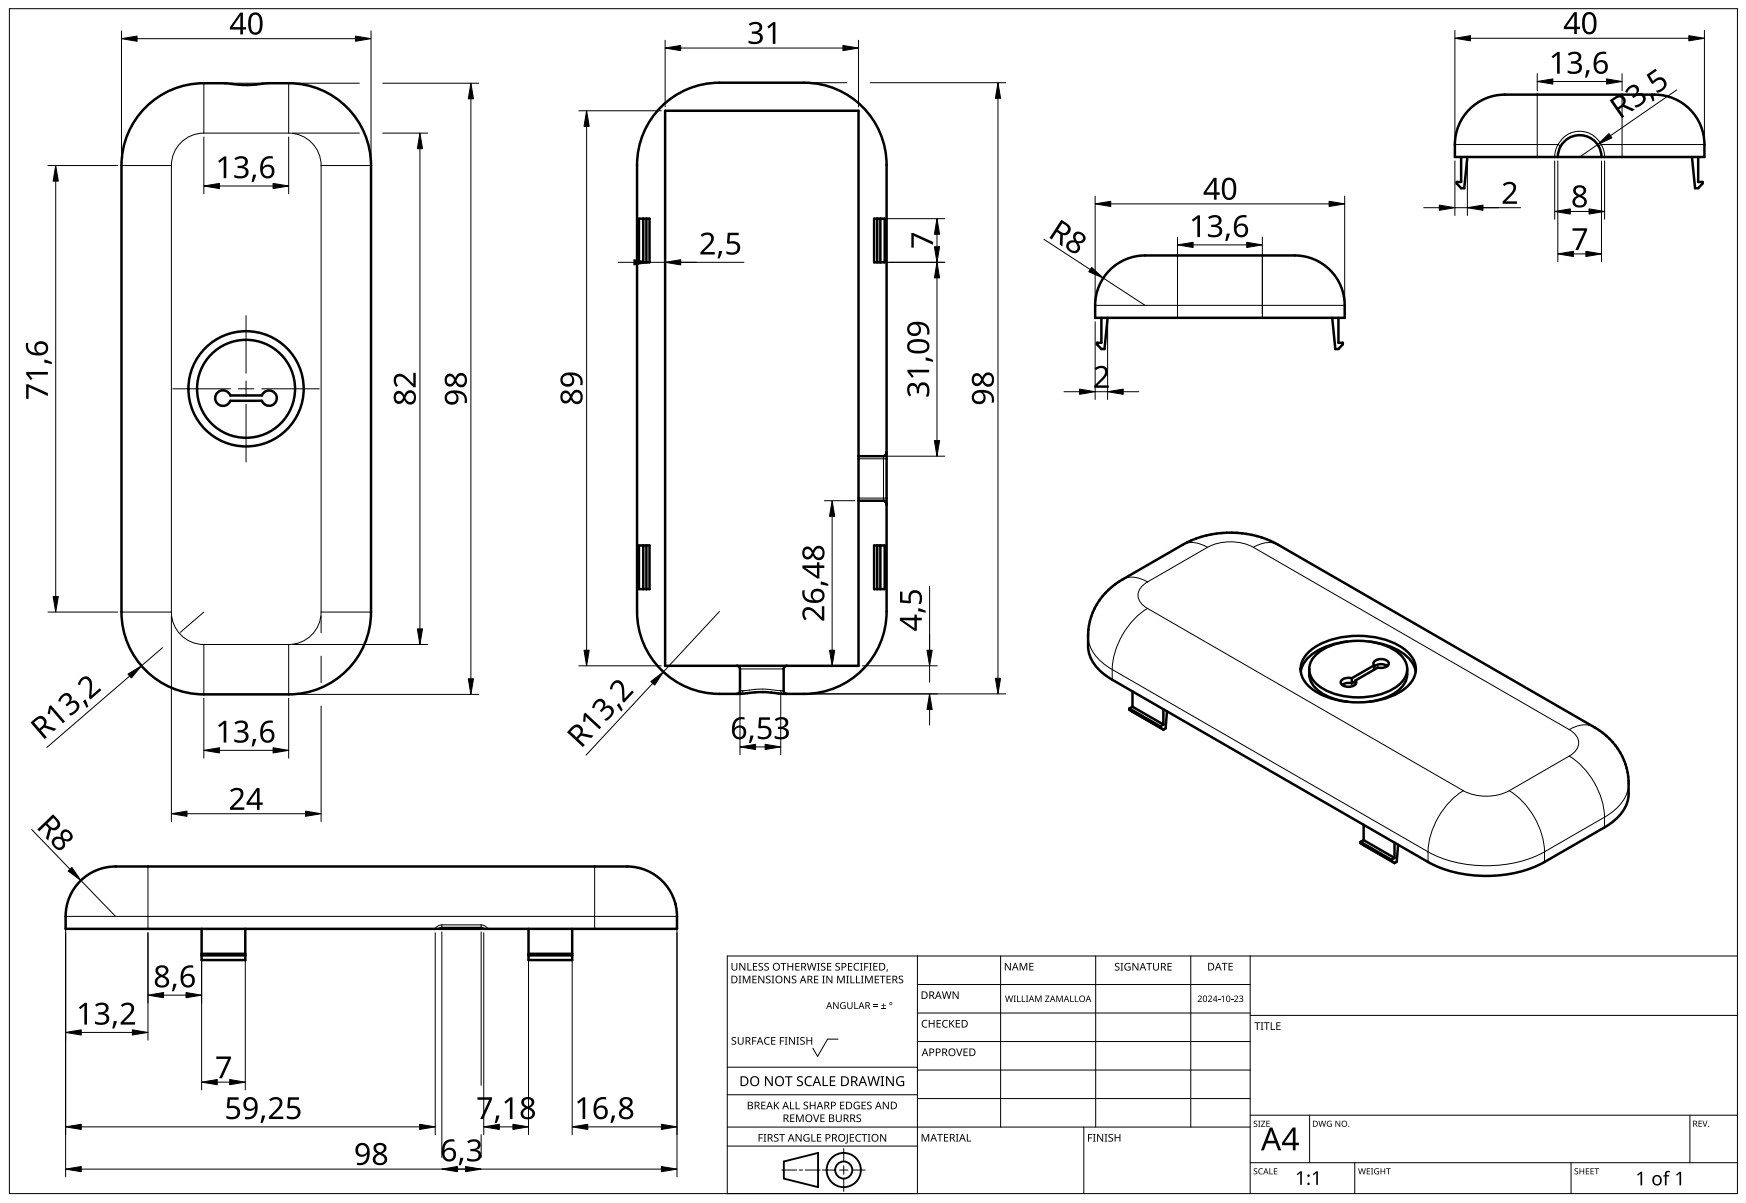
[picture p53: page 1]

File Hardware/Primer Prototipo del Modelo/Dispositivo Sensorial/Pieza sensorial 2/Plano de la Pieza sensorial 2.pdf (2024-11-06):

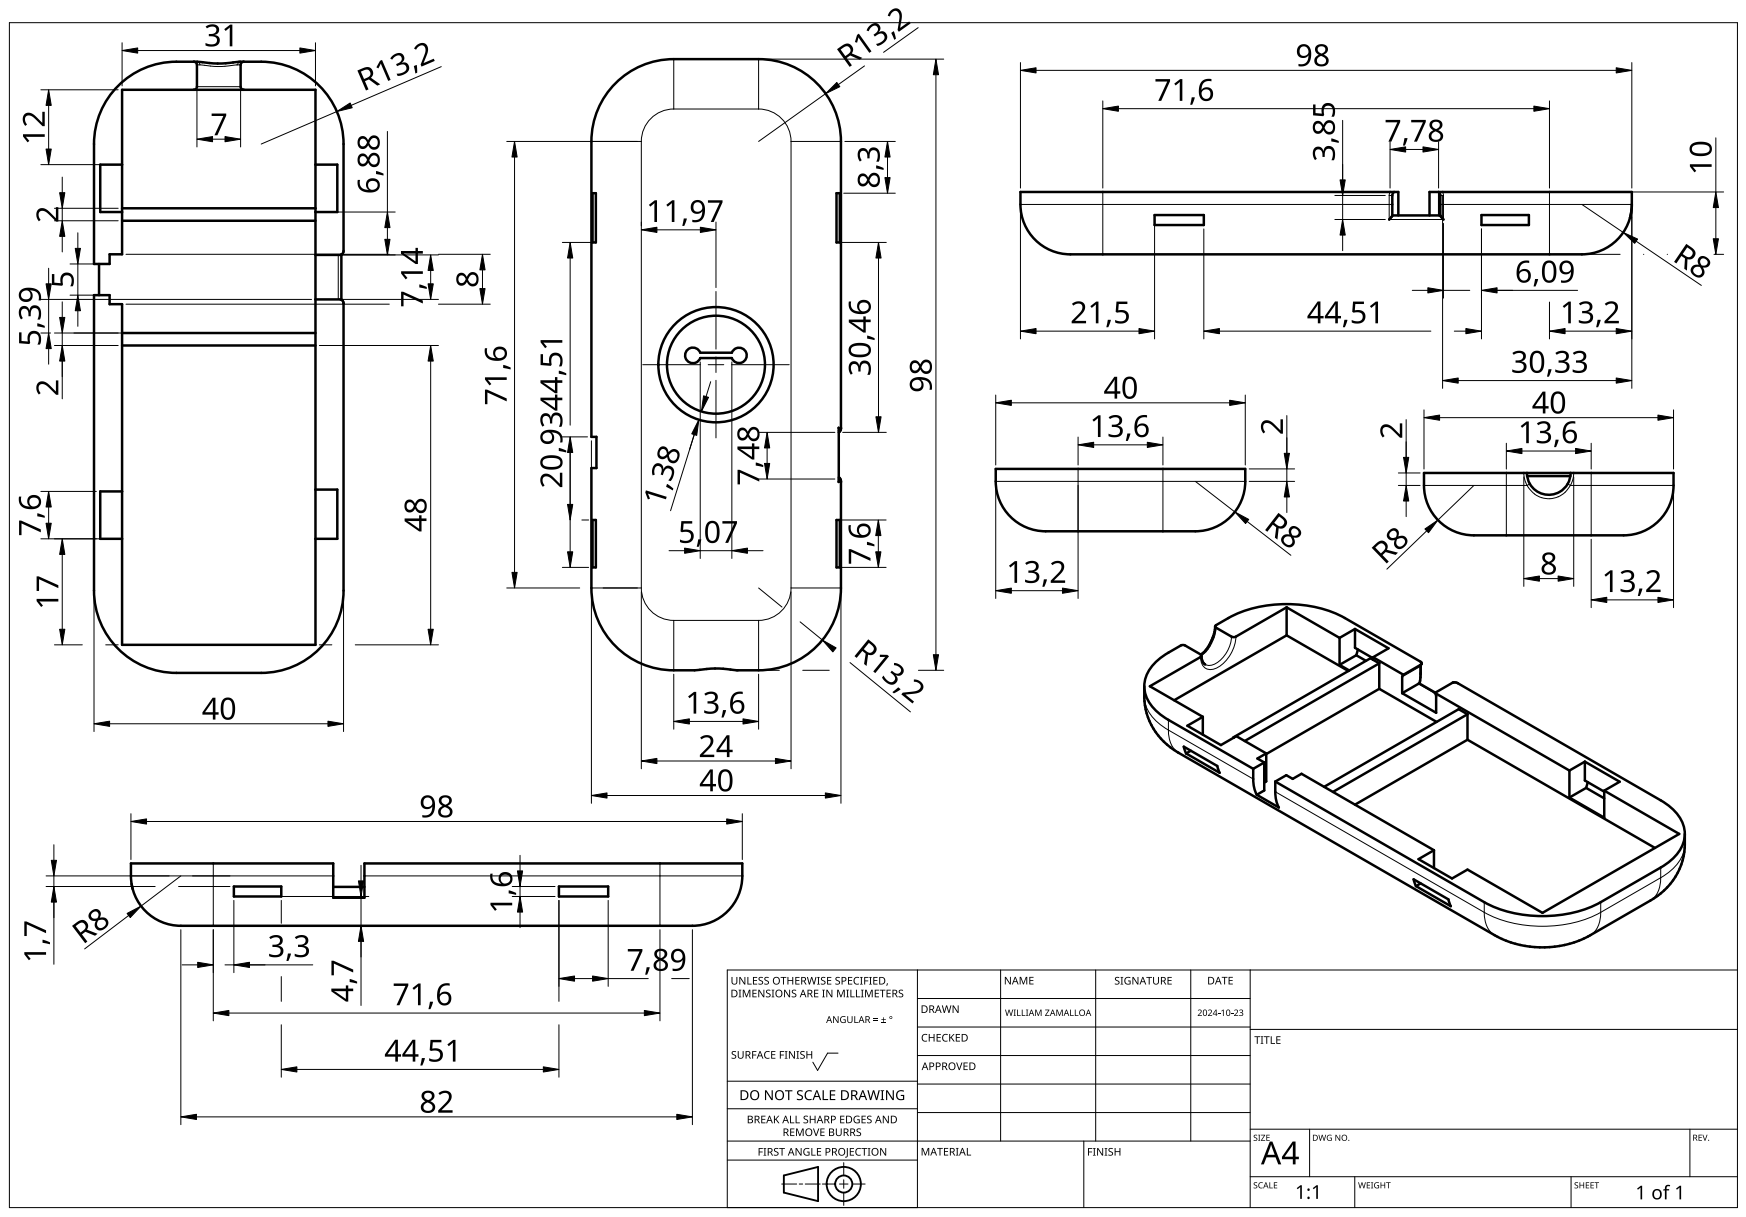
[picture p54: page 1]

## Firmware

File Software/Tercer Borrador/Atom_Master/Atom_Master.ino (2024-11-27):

#include <M5Atom.h>
#include <FastLED.h>
#include <BLEDevice.h>
#include <BLEUtils.h>
#include <BLEClient.h>

#define NUM_LEDS 25
#define DATA_PIN 27

CRGB leds[NUM_LEDS];

// Variables del IMU y ángulos
float baseAngleY = 0;
float lowerLimit1, upperLimit1;
float lowerLimit2, upperLimit2;
float lowerLimit4, upperLimit4;
float deadZoneLower, deadZoneUpper;
int currentRangeState = -1;
bool inDeadZone = false;

// Variables para Bluetooth
static BLEUUID serviceUUID("4fafc201-1fb5-459e-8fcc-c5c9c331914b");
static BLEUUID charUUID("beb5483e-36e1-4688-b7f5-ea07361b26a8");
bool conectado = false;
BLEAddress *pServerAddress;
BLEClient *pClient = nullptr;
BLERemoteCharacteristic *pRemoteCharacteristic = nullptr;

void setup() {
    M5.begin(true, false, true);
    FastLED.addLeds<WS2812, DATA_PIN, GRB>(leds, NUM_LEDS);
    FastLED.clear();
    FastLED.setBrightness(255);

    Serial.begin(115200);

    // Inicialización del IMU
    if (M5.IMU.Init() != 0) {
        Serial.println("Error al inicializar el IMU");
    } else {
        Serial.println("IMU inicializado correctamente");
    }

    // Configuración de Bluetooth
    Serial.println("Iniciando BLE...");
    BLEDevice::init("");
    BLEScan* pBLEScan = BLEDevice::getScan();
    pBLEScan->setActiveScan(true);
    BLEScanResults* foundDevices = pBLEScan->start(5);

    for (int i = 0; i < foundDevices->getCount(); i++) {
        BLEAdvertisedDevice device = foundDevices->getDevice(i);
        if (device.haveServiceUUID() && device.isAdvertisingService(serviceUUID)) {
            Serial.println("Dispositivo esclavo encontrado!");
            pServerAddress = new BLEAddress(device.getAddress());
            conectado = conectarDispositivo();
            break;
        }
    }
    pBLEScan->clearResults();
}

bool conectarDispositivo() {
    pClient = BLEDevice::createClient();
    pClient->connect(*pServerAddress);
    Serial.println("Conectado al esclavo!");

    BLERemoteService *pRemoteService = pClient->getService(serviceUUID);
    if (pRemoteService == nullptr) {
        Serial.println("No se pudo encontrar el servicio.");
        return false;
    }
    pRemoteCharacteristic = pRemoteService->getCharacteristic(charUUID);
    if (pRemoteCharacteristic == nullptr) {
        Serial.println("No se pudo encontrar la característica.");
        return false;
    }
    return true;
}

void setAllLeds(CRGB color) {
    for (int i = 0; i < NUM_LEDS; i++) {
        leds[i] = color;
    }
    FastLED.show();
}

void enviarMensaje(String mensaje) {
    if (conectado) {
        Serial.println("Enviando mensaje al esclavo: " + mensaje);
        pRemoteCharacteristic->writeValue(mensaje.c_str());
    } else {
        Serial.println("Desconectado. Reintentando conexión...");
        conectado = conectarDispositivo();
    }
}

void loop() {
    M5.update();

    if (M5.Btn.wasPressed()) {
        float accelX, accelY, accelZ;
        M5.IMU.getAccelData(&accelX, &accelY, &accelZ);
        baseAngleY = atan2(accelY, accelZ) * 180.0 / PI;

        lowerLimit1 = baseAngleY - 5.0;
        upperLimit1 = baseAngleY + 5.0;
        lowerLimit2 = lowerLimit1 - 30.0;
        upperLimit2 = lowerLimit1;
        lowerLimit4 = upperLimit1;
        upperLimit4 = upperLimit1 + 15.0;
        deadZoneLower = baseAngleY - 30.0;
        deadZoneUpper = baseAngleY + 15.0;

        Serial.println("Rangos actualizados:");
        Serial.printf("Rango 1: [%.2f, %.2f]\n", lowerLimit1, upperLimit1);
        Serial.printf("Rango 2: [%.2f, %.2f]\n", lowerLimit2, upperLimit2);
        Serial.printf("Rango 4: [%.2f, %.2f]\n", lowerLimit4, upperLimit4);
        Serial.printf("Zona Muerta: [%.2f, %.2f]\n", deadZoneLower, deadZoneUpper);
    }

    float accelX, accelY, accelZ;
    M5.IMU.getAccelData(&accelX, &accelY, &accelZ);
    float currentAngleY = atan2(accelY, accelZ) * 180.0 / PI;

    int newRangeState = -1;
    if (!inDeadZone && currentAngleY < deadZoneLower) {
        inDeadZone = true;
        enviarMensaje("Zm");
        setAllLeds(CRGB::Purple);
    } else if (inDeadZone && currentAngleY > deadZoneUpper) {
        inDeadZone = false;
    }

    if (!inDeadZone) {
        if (currentAngleY >= lowerLimit1 && currentAngleY < upperLimit1) {
            newRangeState = 1;
        } else if (currentAngleY >= lowerLimit2 && currentAngleY < upperLimit2) {
            newRangeState = 2;
        } else if (currentAngleY >= lowerLimit4 && currentAngleY <= upperLimit4) {
            newRangeState = 4;
        }
    }

    if (newRangeState != currentRangeState) {
        currentRangeState = newRangeState;
        if (currentRangeState == 1) {
            enviarMensaje("P0");
            setAllLeds(CRGB::Green);
        } else if (currentRangeState == 2) {
            enviarMensaje("P1");
            setAllLeds(CRGB::Yellow);
        } else if (currentRangeState == 4) {
            enviarMensaje("P2");
            setAllLeds(CRGB::Blue);
        }
    }

    delay(10);
}

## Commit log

2024-08-25 Añadir la carpeta Hardware al repositorio
2024-08-25 Eliminar la carpeta
2024-08-25 Eliminacion de la carpeta de prueba Entregable 1
2024-08-26 Añadir foto para la presentación
2024-08-26 Eliminar el archivo temporal .gitkeep
2024-08-26 Prueba para la presentacion
2024-08-26 Actuazlicacion de Readme
2024-08-27 Actualización de imagenes para el Entregable 1
2024-09-03 Actualización de imagenes para el Entregable 2
2024-09-04 Actualizacion de imagenes para el Entregable 2
2024-09-04 Actualizacion de imagenes del Entregable 2
2024-09-17 Actualización de imagenes del Entregable 1
2024-09-17 Actualizacion de imagenes del Entregable 1
2024-09-17 Actualizacion de imagenes para el Entregable 1
2024-09-25 Actualizacion de imagenes del Entregable 4
2024-09-25 Actualizacion de imagenes para el Entregable 4
2024-10-08 Actualizacion de imagenes
2024-10-09 Actualizacion de los Resources
2024-10-23 Actualizacion para el Hito 1
2024-11-06 Actualizacion de Entregable 6
2024-11-06 Actualizacion del Diseño 3D
    [Pieza de medicion 1.stl, Pieza de medicion 2.stl, Pieza sensorial 1.stl, Pieza sensorial 2.stl]
2024-11-13 Actualizacion de la carpeta Software
2024-11-19 Actualizacion de Diseño3D y Software
    [Pieza de medicion 1.stl, Pieza de medicion 2.stl]
2024-11-20 Actualizacion de Entregables
2024-11-27 Actualizaciones para el Hito 2
    [Parte de la base.stl, Parte de la tapa.stl, Parte del cuerpo.stl, Pieza de medicion 1.stl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]
